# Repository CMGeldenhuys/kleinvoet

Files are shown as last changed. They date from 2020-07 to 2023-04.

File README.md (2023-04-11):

# Kleinvoet





*Kleinvoet* is a self-contained low-cost passive acoustic monitoring device.
The recorder was initially designed for distributed infrasonic (8Hz)
localisation, and features accurate temporal synchronisation through the use of
an onboard GNSS module.

The recorder is capable of 24-bit stereo recording at a variable sampling rate
of 8kHz to 192kHz.  The recordings along with timestamp and operational log
information is stored on a microSD card.  The recordings are stored as a series of
256MiB WAV files.

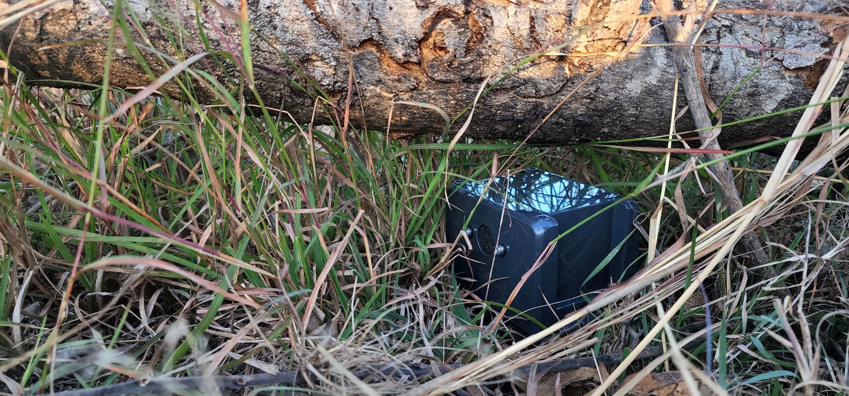
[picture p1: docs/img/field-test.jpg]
Kleinvoet Field Test


Firmware is available at [CMGeldenhuys/kleinvoet-firmware](https://github.com/CMGeldenhuys/kleinvoet-firmware).
All relevant production files such as panelised gerbers, bill of materials and work orders can be found in the `production` folder in the repo.
Additionally, the PCB layout and schematics for the Kleinvoet recorders can be found in the `docs/pcb_single`, `docs/pcb_panel` and `docs/schematics` directories, respectively.

## Example Recordings

- [Artificial elephant call](docs/rec/elephant_call_1000hz_lpf_normalised.wav) (recorded 150m from source, 1000Hz low pass filtered and normalised)

## SD Card Recommendations

In order to keep cost down, Kleinvoet does not make use of external SRAM. As such
the I/O buffer is limited to the internal SRAM of the MCU. It is thus
recommended using a class-10 high quality microSD card. Before a long-running
experiment it is also recommended to do a "low-level" format of the microSD
card. This will improve the write performance which is required at higher
sampling rates.

## Assembly

To assemble a Kleinvoet node, one will require all the electronic
components listed in the bill of materials (BOM), as well as have the necessary
PCBs manufactured. The provided gerber files can be sent directly to most PCB
fabrication houses. To assemble the boards, one can use either hot-air or plate
reflow soldering methods. The [interactive BOM](bom/ibom.html) might be useful
when placing the components manually.

| PCB | Back | Front |
| --- | --- | --- |
|Main Board|  |  |
|GNSS Board|  |  |
|Microphone Board|  |  |

Once all the components have been soldered to their respective boards, the
firmware can be flashed to the MCU using an [ST
Link](https://www.st.com/en/development-tools/st-link-v2.html)
debugger/programmer. However, not tested, any JTAG debugger/programmer should
work. There are also open-source projects that use another STM32 MCU as a
debugger/programmer ([blackmagic
probe](https://github.com/blackmagic-debug/blackmagic)).

Once programmed, proceed by connecting the GNSS header (marked on the respective
PCBs) of the main board to the GNSS daughter board. Note, this connector can be
reversed and the user should double-check that the **SYNC** pin (marked with an
triangle) on the main board is connected to the **SYNC** pin of the GNSS board.
If your use case does not require timestamping, the GNSS board can be omitted.
Next, connect the microphone boards to their respective channels, marked on the
main board's PCB as **CH1** and **CH2**. These connectors are keyed, and thus
It can only be connected one way.

If the user chooses to omit the weatherproof housing, Kleinvoet can be held
together with two rubber bands. The notches on the main and GNSS boards snap
together with the holes in the microphone boards to form a cube.



In order to assemble the weatherproof housing, start by placing the LiPo battery
in the lid of the enclosure. Thread the battery lead through the hole of the
main PCB adaptor plate. Next, mount the plate to the lid, keeping the battery in
place. One can then proceed to mount the main PCB to the adaptor. Next mount
the GNSS adaptor plate in the bottom of the Bocube housing, and mount the GNSS
PCB to the adaptor. If using the windshielding, remove the backing paper and
paste it firmly over the microphone inlets, (Note, the MEMS microphones used are
bottom port microphone and thus the inlet port is on the bottom side of the PCB.
The area to place the shielding foam is marked by a hashed circle) Install the
microphone board spacers, ensuring that the mounting holes align properly. The
microphone board assembly can now be mounted to the inside of the Bocube
housing. Next, connect the individual daughter boards (GNSS and microphone PCBs)
to their respective connectors on the main board.

Insert a FAT32 formatted microSD card into the main board and plug in the
battery. The node will perform a self test, followed by a self configuration
stage and then begin recordings. This process might take up to 10 seconds. Once
the node is configured, a solid amber light will be illuminated. Please refer to
the troubleshooting section if this is not the case.

## Operation

### Startup Procedure

1. Ensure the device is powered off.
1. Insert a FAT32 formatted microSD into the main board.
1. Connect the battery to the main board.
1. Wait for the solid amber indicator LED.
1. (Optional) Close weatherproof housing.

### Shutdown Procedure

1. Press the **USER** button (marked on the PCB of the main board).
1. The status indicators should start flashing repeatedly.
1. Disconnect the battery.
1. Remove microSD card.

### Status Indicators
Each PCB contains a *RED* status LED, used to indicate that the board has power.
On the main PCB there are two running status indication LEDs (*AMBER* and *BLUE*).

When **running**, the *AMBER* LED will remain solid. Once a GNSS lock (both time
and location) is obtained, the *BLUE* LED will pulse briefly every 10 seconds
(default).

If an unrecoverable error has occurred, the two status LEDs (*AMBER* and *BLUE*),
will pulse is quick succession. In this case, the watchdog timer will trigger and
attempt to write the operational log and reset the device. During a catastrophic
failure it might not be possible to write to the microSD card depending on the
error that has occurred.

| State | Blue LED | Amber LED |
| --- | --- | --- |
| Start-up | Blink (1s) | Off |
| Recording | Solid | X |
| GNSS Lock | X | Blink (10s) |
| Catastrophic Error | Strobe | Strobe |

In the table above, '*X*' denotes a "do not care" or irrelevant status. In other
words, it is not an indication of the current device state.

### File Layout

After recording, the following file structure will be present on the microSD card of the respective node.

```
(root)
├── REC_1
│   ├── KV.LOG
│   ├── REC.WAV
│   ├── REC.W01
│   ├── REC.W02
│   ├── REC.W03
│   └── TS.CSV
├── REC_X
│   ├── KV.LOG
│   ├── REC.WXX
│   └── TS.CSV
└── CONF.INI (experimental)
```

Each recording will be stored as a WAVE file in the corresponding `REC_X`
folder. Where the recorder increments `X` for every subsequent recording made on
the device (e.g. `REC_1`, `REC_2` etc.). Inside each recording folder are the
files associated with that recording. Due to the limitation of the FAT32
filesystem each individual recording has to be split up across multiple WAVE
files (e.g.`REC.WAV`, `REC.W01`, etc.). By default, this is in 256 MiB chunks, but
is user configurable Contained in the header of each WAVE file is timestamping
and location information required to synchronise the nodes during offline
processing of the files. A granular log of the timestamping metadata is stored
in `TS.CSV`. A complete operational log is stored in `KV.LOG`, which might deem
useful in troubleshooting a faulty recording node. (Experimental) Currently the
node's configuration is compiled into the device firmware, however, there is a
experimental firmware branch that allows for the configuration to be stored on
the microSD. 

| File/Folder | Purpose |
| --- | --- |
| REC_X | Folder containing all files associated with the particular recording|
| KV.LOG | Operational log of recordings |
| TS.CSV | Timestamping metadata |
| REC.WXX | Audio recording stored as a WAVE file |
| CONF.INI | (Experimental) Runtime configuration file |

## Power Spectral Density Estimates

Provided below are a power spectral density estimates (PSD) generated using
Welch's method. The [Sennheiser MKH 8020](https://sennheiser.com/mkh-8020) was used as a reference microphone and
tested in an acoustically dampened recording studio. These results provide an
estimate of the recording device's frequency response and should not be used
as ground truth measurements where spectral magnitude accuracy is required.
For those types of experiments, we recommenced the use of calibrated reference
sound amplitude measurement equipment.

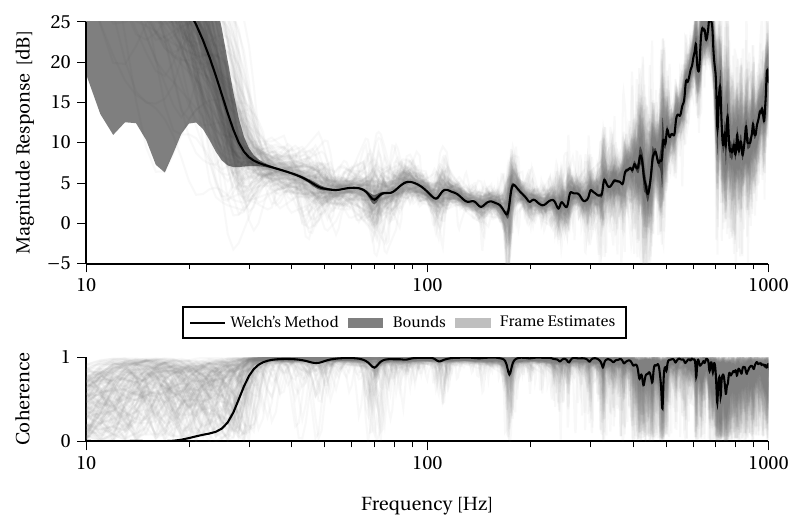
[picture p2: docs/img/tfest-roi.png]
Power Spectral Density Estimate


## Troubleshooting

First ensure the following:
- Power from USB-C not battery, all boards have a solid *RED* LED illuminated
- MicroSD Card is formatted as **FAT32** and inserted
- The respective daughter boards are correctly connected

Enable `LOG_DEST_TTY` in `config.h`. The operational log will be printed in
real-time to the serial console available on the debug/programming port. When
using an *ST Link* debugger, this serial port can be opened using
[Putty](https://www.putty.org/) on Windows, or with the following command on
Linux:
``` sh
screen -b 115200 /dev/ttyACM0
```
The serial port is configured to **115200** baud rate and the standard **8N1**
configuration. Please see the [firmware guide](firmware/README.md) for more
information on setting up the programming environment on a Linux-based system.

## Future Hardware Revisions

- [ ] Dedicated GNSS connector, instead of headers
- [ ] E-Ink Display
- [ ] DFU mode (program without probe)
- [ ] Improved low-power mode (deep sleep)
- [ ] Add BME280 Sensor (temperature, humidity, atmospheric pressure)
- [ ] Battery charging status detection
- [ ] Dedicated power switch
- [ ] External RAM (larger buffer, allows use with low-end SD cards)
- [ ] Allow non-LiPo batteries (eg. alkaline)

## Contributing

We welcome contributions to the project. Unfortunately, hardware cannot be
provided to contributors. However, the [STM32
Nucleo-F446RE](https://www.st.com/en/evaluation-tools/nucleo-f446re.html) can be
used as an firmware development alternative, and is readily available.

## Authors and Acknowledgements

- [Christiaan M. Geldenhuys](https://github.com/CMGeldenhuys)
- [Thomas R. Niesler](https://dsp.sun.ac.za/~trn)

This project formed part of research done by the [Electrical and Electronic
Engineering Department](https://www.ee.sun.ac.za/) at Stellenbosch University.

Stellenbosch University Logo (https://www.ee.sun.ac.za/)

## License

The Kleinvoet project is licensed under the CERN Open Hardware License version 2
(strongly-reciprocal variant). The license agreement and copyright only partain
to the Kleinvoet recorder design. Third party CAD models and EDA footprints
remain under the original license agreement and copyright of the respective
intellectual property owners.

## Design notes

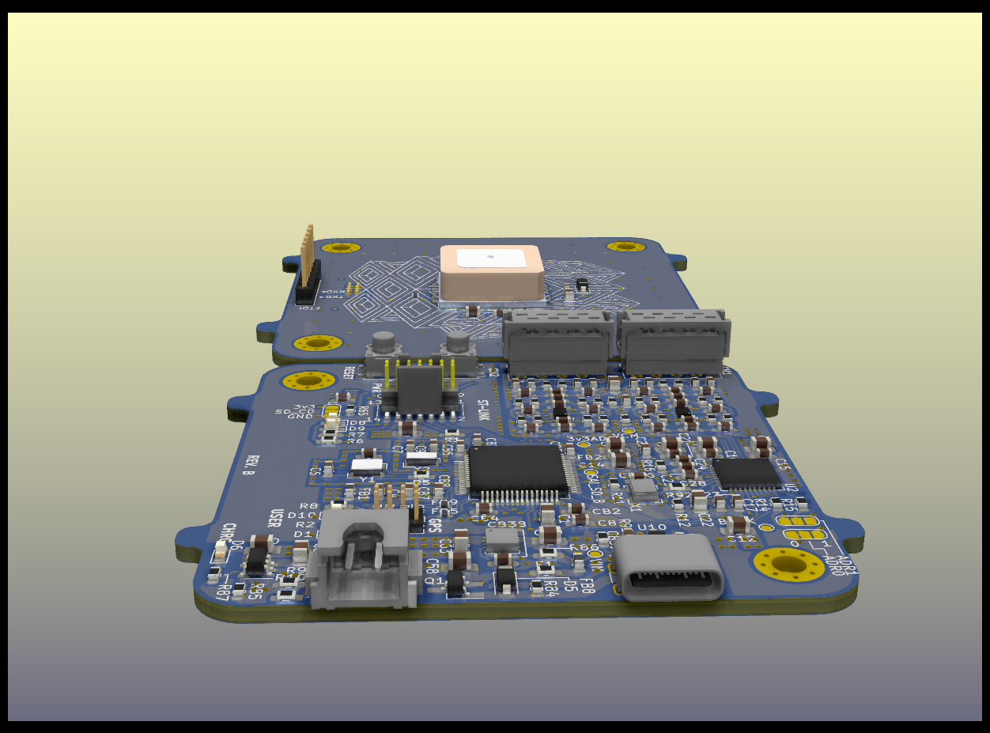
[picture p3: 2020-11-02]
docs/img/kleinvoet_render_3.png

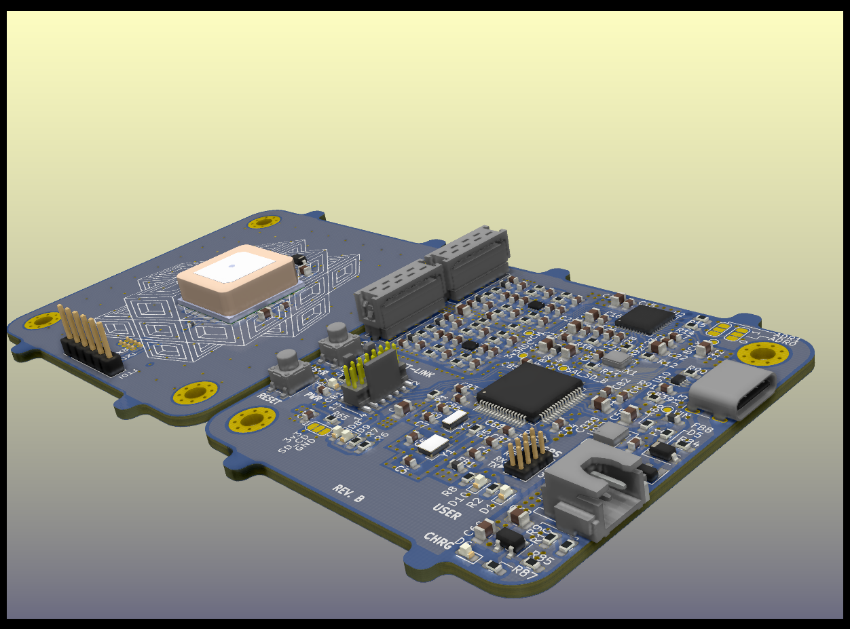
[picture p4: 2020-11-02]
docs/img/kleinvoet_render_0.png

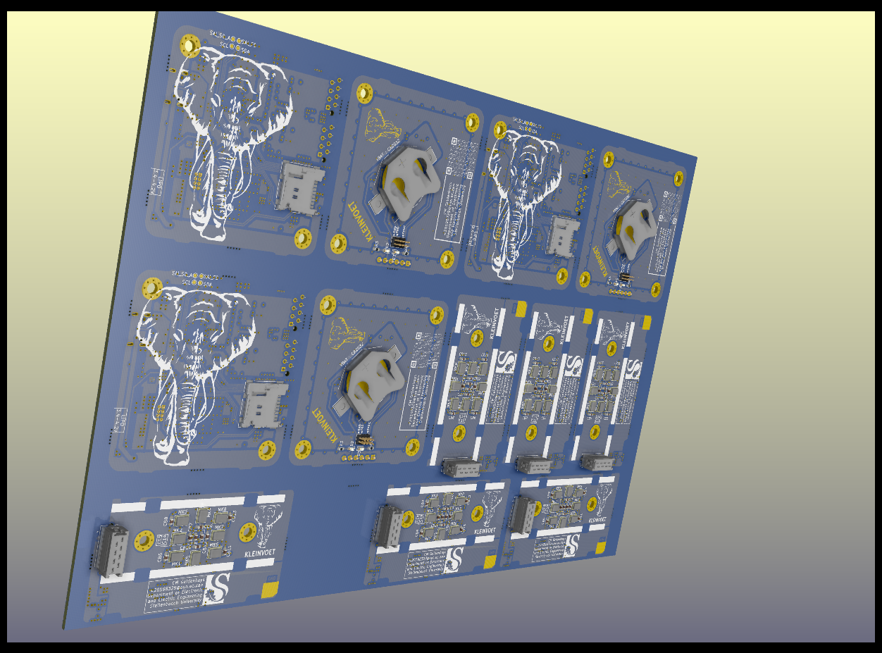
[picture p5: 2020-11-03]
docs/img/panel_render_1.png

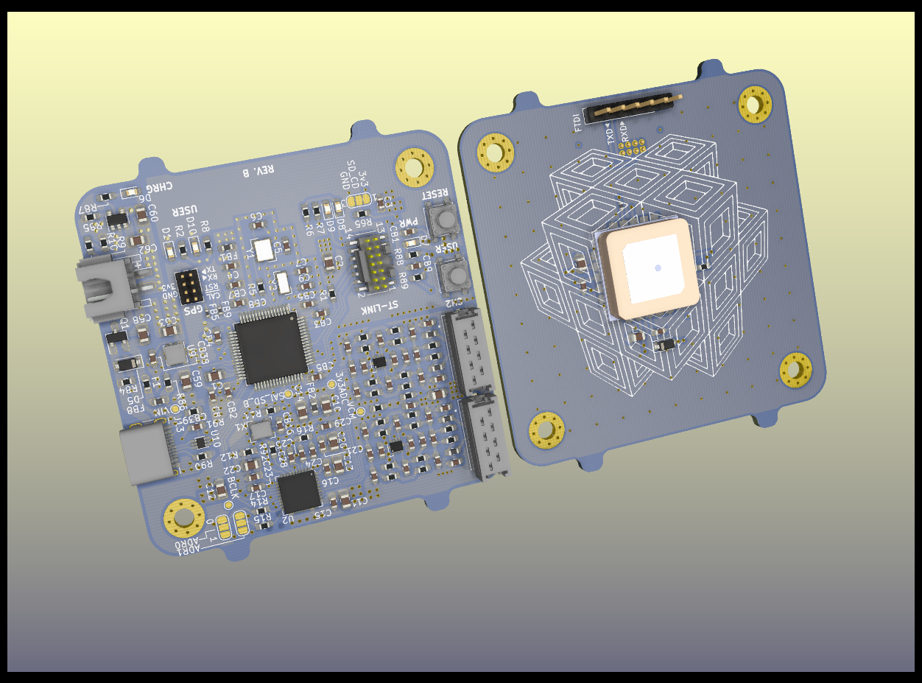
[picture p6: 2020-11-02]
docs/img/kleinvoet_render_1.png

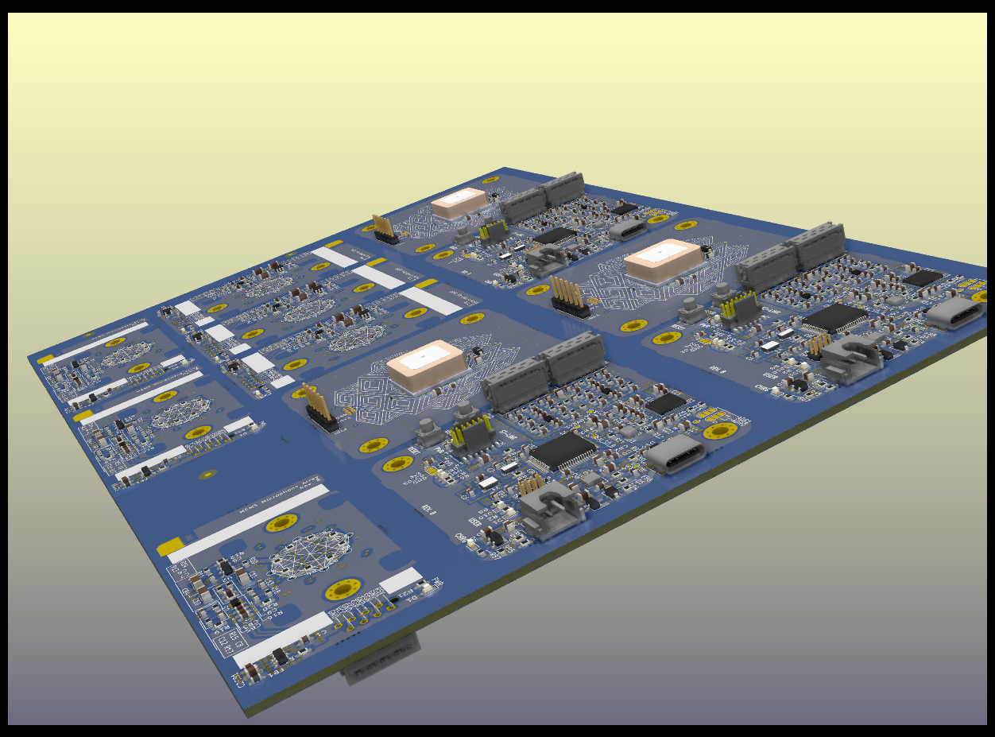
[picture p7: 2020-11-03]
docs/img/panel_render_0.png

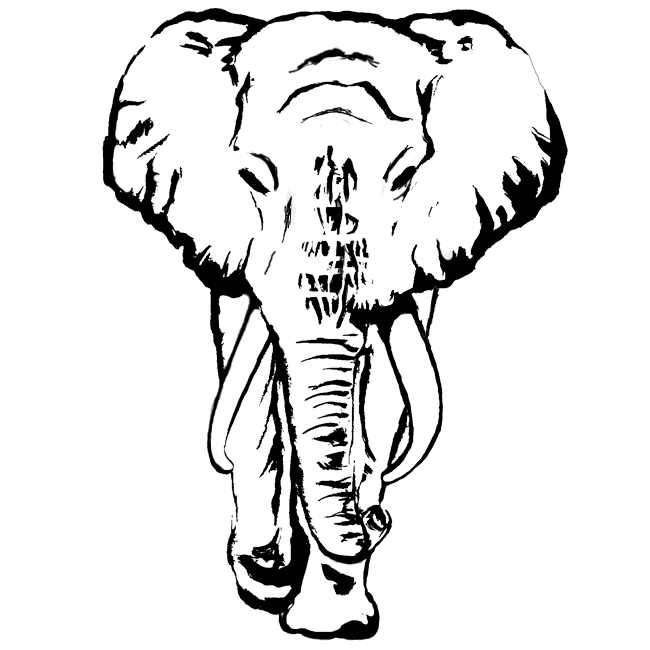
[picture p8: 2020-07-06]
docs/img/oli2.bmp

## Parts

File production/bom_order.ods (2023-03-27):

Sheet: FAB
Received | MPN | Mfr. | Board | Quantity | Value | Reference
1 | 7-215079-8 | TE Connectivity | Sensor_Board_1 | 1 | Sensor_Conn | J1
1 | 7-215083-8 | TE Connectivity | Sensor_Board_1 | 1 | Sensor_Conn | J1
1 | BLM18EG101TZ1D | Murata Electronics | Sensor_Board_1 | 1 | 100 @ 100 MHz | FB1
1 | C0603C104M5RACTU | KEMET | Sensor_Board_1 | 12 | 100n | CB1 CB10 CB11 CB12 CB13 CB3 CB4 CB5 CB6 CB7 CB8 CB9
1 | C0603C105K8RACTU | KEMET | Sensor_Board_1 | 4 | 1u | C1 C14 C15 C3
1 | C0603C221J5GACTU | KEMET | Sensor_Board_1 | 3 | 220p | C12 C13 C5
1 | C0805C106K9PACTU | KEMET | Sensor_Board_1 | 1 | 10u | C2
1 | CC0603JRX7R8BB183 | Yageo | Sensor_Board_1 | 1 | 18n | C6
1 | CC0603JRX7R9BB272 | Yageo | Sensor_Board_1 | 2 | 2.7n | C8 C9
1 | ERJ-3EKF1001V | Panasonic | Sensor_Board_1 | 2 | 1k0 | R17 R18
1 | ERJ-3EKF2100V | Panasonic | Sensor_Board_1 | 1 | 210 | R14
1 | ERJ-3EKF2201V | Panasonic | Sensor_Board_1 | 11 | 2k2 | R11 R12 R2 R21 R3 R4 R5 R6 R7 R8 R9
1 | ERJ-3EKF2700V | Panasonic | Sensor_Board_1 | 1 | 270 | R13
1 | ERJ-3EKF3300V | Panasonic | Sensor_Board_1 | 2 | 330 | R15 R16
1 | ERJ-3EKF47R0V | Panasonic | Sensor_Board_1 | 2 | 47 | R19 R20
1 | GRM31CR60J107KE39K | Murata Electronics | Sensor_Board_1 | 3 | 47u | C10 C11 C4
1 | ICS-40300 | TDK InvenSense | Sensor_Board_1 | 9 | TestPoint | MK1 MK2 MK3 MK4 MK5 MK6 MK7 MK8 TP1
1 | OPA377AIDBVR | Texas Instruments | Sensor_Board_1 | 1 | OPA377xxDBVx | U2
1 | RC0603JR-0710KL | Yageo | Sensor_Board_1 | 1 | 10k | R1
1 | SML-D12U8WT86C | ROHM Semiconductor | Sensor_Board_1 | 1 | RED | D1
1 | THS4551IRUNR | Texas Instruments | Sensor_Board_1 | 1 | THS4551 | U3
1 | TLV74118PDBVR | Texas Instruments | Sensor_Board_1 | 1 | TLV741PxxDBVx | U1
1 | 7-215079-8 | TE Connectivity | Sensor_Board_2 | 1 | Sensor_Conn | J1
1 | 7-215083-8 | TE Connectivity | Sensor_Board_2 | 1 | Sensor_Conn | J1
1 | BLM18EG101TZ1D | Murata Electronics | Sensor_Board_2 | 1 | 100 @ 100 MHz | FB1
1 | C0603C104M5RACTU | KEMET | Sensor_Board_2 | 12 | 100n | CB1 CB10 CB11 CB12 CB13 CB3 CB4 CB5 CB6 CB7 CB8 CB9
1 | C0603C105K8RACTU | KEMET | Sensor_Board_2 | 4 | 1u | C1 C14 C15 C3
1 | C0603C221J5GACTU | KEMET | Sensor_Board_2 | 3 | 220p | C12 C13 C5
1 | C0805C106K9PACTU | KEMET | Sensor_Board_2 | 1 | 10u | C2
1 | CC0603JRX7R8BB183 | Yageo | Sensor_Board_2 | 1 | 18n | C6
1 | CC0603JRX7R9BB272 | Yageo | Sensor_Board_2 | 2 | 2.7n | C8 C9
1 | ERJ-3EKF1001V | Panasonic | Sensor_Board_2 | 2 | 1k0 | R17 R18
1 | ERJ-3EKF2100V | Panasonic | Sensor_Board_2 | 1 | 210 | R14
1 | ERJ-3EKF2201V | Panasonic | Sensor_Board_2 | 11 | 2k2 | R11 R12 R2 R21 R3 R4 R5 R6 R7 R8 R9
1 | ERJ-3EKF2700V | Panasonic | Sensor_Board_2 | 1 | 270 | R13
1 | ERJ-3EKF3300V | Panasonic | Sensor_Board_2 | 2 | 330 | R15 R16
1 | ERJ-3EKF47R0V | Panasonic | Sensor_Board_2 | 2 | 47 | R19 R20
1 | GRM31CR60J107KE39K | Murata Electronics | Sensor_Board_2 | 3 | 47u | C10 C11 C4
1 | ICS-40300 | TDK InvenSense | Sensor_Board_2 | 9 | TestPoint | MK1 MK2 MK3 MK4 MK5 MK6 MK7 MK8 TP1
1 | OPA377AIDBVR | Texas Instruments | Sensor_Board_2 | 1 | OPA377xxDBVx | U2
1 | RC0603JR-0710KL | Yageo | Sensor_Board_2 | 1 | 10k | R1
1 | SML-D12U8WT86C | ROHM Semiconductor | Sensor_Board_2 | 1 | RED | D1
1 | THS4551IRUNR | Texas Instruments | Sensor_Board_2 | 1 | THS4551 | U3
1 | TLV74118PDBVR | Texas Instruments | Sensor_Board_2 | 1 | TLV741PxxDBVx | U1
1 | 0ZCM0020FF2G | Bel Fuse | kleinvoet | 1 | 400mA | F1
1 | 1769 | Adafruit | kleinvoet | 1 | JST-PH | J12
1 | 2898 | Keystone Electronics | kleinvoet | 1 | COIN_BAT | BT1
1 | 7-215079-8 | TE Connectivity | kleinvoet | 2 | Sensor_Conn | J3 J6
1 | 7-215083-8 | TE Connectivity | kleinvoet | 2 | Sensor_Conn | J3 J6
1 | AC0603FR-135K1L | Yageo | kleinvoet | 3 | 5.1k | R85 R90 R91
1 | ADAU1978WBCPZ-RL | Analog Devices | kleinvoet | 1 | ADAU1978 | U2
1 | BLM15HD102SN1D | Murata Electronics | kleinvoet | 3 | BLM15HD102SN1 | FB10 FB5 FB9
1 | BLM18EG101TZ1D | Murata Electronics | kleinvoet | 1 | 100 @ 100 MHz | FB8
1 | BLM18KG101TZ1D | Murata Electronics | kleinvoet | 2 | BLM18KG101TZ1D | FB1 FB2
1 | BLM18KG102SN1D | Murata Electronics | kleinvoet | 4 | 1k @ 100 MHz | FB11 FB3 FB4 FB7
1 | C0603C103J5RACTU | KEMET | kleinvoet | 6 | 10n | C42 C44 C76 C78 CB38 CB8
1 | C0603C104M5RACTU | KEMET | kleinvoet | 24 | 100n | C15 C16 C17 C21 C23 C28 C29 C37 C40 C43 C71 C74 C77 CB1 CB16 CB2 CB3 CB39 CB4 CB40 CB5 CB6 CB7 CB9
1 | C0603C105K8RACTU | KEMET | kleinvoet | 5 | 1u | C3 C32 C4 C66 C8
1 | C0603C150J5GACTU | KEMET | kleinvoet | 2 | 15pF | C5 C6
1 | C0603C221J5GACTU | KEMET | kleinvoet | 8 | 220p | C18 C19 C26 C27 C30 C31 C61 C67
1 | C0805C106K9PACTU | KEMET | kleinvoet | 17 | 10u | C1 C10 C11 C12 C13 C14 C2 C20 C22 C33 C58 C59 C60 C62 C63 C64 C65
1 | C1608C0G1H040C080AA | TDK | kleinvoet | 2 | 4p | C7 C9
1 | CC0603JRNPO9BN391 | Yageo | kleinvoet | 1 | 390p | C25
1 | CC0603JRX7R9BB273 | Yageo | kleinvoet | 2 | 27n | C34 C68
1 | CC0603JRX7R9BB392 | Yageo | kleinvoet | 4 | 3.9n | C38 C39 C72 C73
1 | CC0603JRX7R9BB562 | Yageo | kleinvoet | 1 | 5.6n | C24
1 | DX07S016JA1R1500 | JAE Electronics | kleinvoet | 1 | USB_C_Receptacle_USB2.0 | J13
1 | ECS-.327-7-34B-TR | ECS | kleinvoet | 1 | 32.768 kHz | Y2
1 | ECS-120-12-33-AEN-TR | ECS | kleinvoet | 1 | 12 MHz | Y1
1 | ECS-TXO-3225MV-122.8-TR | ECS | kleinvoet | 1 | 12.288MHz | X1
1 | ERJ-3EKF15R0V | Panasonic | kleinvoet | 4 | 15 | R25 R26 R49 R50
1 | ERJ-3EKF3090V | Panasonic | kleinvoet | 4 | 310 | R17 R18 R41 R42
1 | ERJ-3EKF3300V | Panasonic | kleinvoet | 4 | 330 | R21 R22 R45 R46
1 | ERJ-3EKF3600V | Panasonic | kleinvoet | 4 | 360 | R23 R24 R47 R48
1 | ERJ-3EKF47R0V | Panasonic | kleinvoet | 6 | 47 | R20 R27 R28 R51 R52 R92
1 | FTSH-104-01-F-D | Samtec | kleinvoet | 2 | GPS_Transmission_Conn | J16 J4
1 | FTSH-107-01-F-DV-K | Samtec | kleinvoet | 1 | Conn_ST_STDC14 | J1
1 | MCP73831T-2ACI/OT | Microchip | kleinvoet | 1 | MCP73831-2-OT | U8
1 | NTR3A30PZT1G | ON Semiconductor | kleinvoet | 1 | PMOS | Q1
1 | PTS647SN50SMTR2LFS | C&K | kleinvoet | 2 | USER | SW1 SW2
1 | RC0603FR-07100KL | Yageo | kleinvoet | 4 | 100k | R13 R19 R65 R84
1 | RC0603FR-071KL | Yageo | kleinvoet | 1 | 1k | R16
1 | RC0603FR-072K2L | Yageo | kleinvoet | 8 | 2.2k | R2 R3 R4 R6 R7 R8 R87 R88
1 | RC0603FR-07470KL | Yageo | kleinvoet | 2 | 500k | R10 R9
1 | RC0603FR-1068RL | Yageo | kleinvoet | 1 | 68 | R5
1 | RC0603JR-0710KL | Yageo | kleinvoet | 7 | 10k | R1 R11 R12 R14 R15 R86 R89
1 | RSX101MM-30TR | ROHM Semiconductor | kleinvoet | 2 | Vf low | D4 D5
1 | SML-D12D8WT86C | ROHM Semiconductor | kleinvoet | 2 | ORANGE | D10 D6
1 | SML-D12U8WT86C | ROHM Semiconductor | kleinvoet | 1 | RED | D7
1 | SML-D12Y8WT86C | ROHM Semiconductor | kleinvoet | 2 | YELLOW | D3 D9
1 | SMLD12BN1WT86 | ROHM Semiconductor | kleinvoet | 1 | BLUE | D1
1 | SMLD12EN1WT86 | ROHM Semiconductor | kleinvoet | 2 | GREEN | D2 D8
1 | STM32F446RCT6 | STMicroelectronics | kleinvoet | 1 | STM32F446RETx | U1
1 | THS4551IRUNR | Texas Instruments | kleinvoet | 2 | THS4551 | U3 U5
1 | TPS73733QDRBRQ1 | Texas Instruments | kleinvoet | 1 | TPS73733QDRBRQ1 | U9
1 | USBLC6-2P6 | STMicroelectronics | kleinvoet | 1 | USBLC6-2SC6 | U10

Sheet: Data
Board | Reference | Value | Footprint | Datasheet | MPN | Mfr. | Notes
kleinvoet | C2 | 10u | Capacitor_SMD:C_0805_2012Metric_Pad1.18x1.45mm_HandSolder | ~ | C0805C106K9PACTU | KEMET | Low ESR
kleinvoet | CB2 | 100n | Capacitor_SMD:C_0603_1608Metric_Pad1.08x0.95mm_HandSolder | ~ | C0603C104M5RACTU | KEMET
kleinvoet | FB1 | BLM18KG101TZ1D | Inductor_SMD:L_0603_1608Metric_Pad1.05x0.95mm_HandSolder | ~ | BLM18KG101TZ1D | Murata Electronics | 100 @ 100 MHz
kleinvoet | CB7 | 100n | Capacitor_SMD:C_0603_1608Metric_Pad1.08x0.95mm_HandSolder | ~ | C0603C104M5RACTU | KEMET | Low ESR (X7R)
kleinvoet | C4 | 1u | Capacitor_SMD:C_0603_1608Metric_Pad1.08x0.95mm_HandSolder | ~ | C0603C105K8RACTU | KEMET | Low ESR (X7R)
kleinvoet | CB8 | 10n | Capacitor_SMD:C_0603_1608Metric_Pad1.08x0.95mm_HandSolder | ~ | C0603C103J5RACTU | KEMET | Low ESR (X7R)
kleinvoet | CB3 | 100n | Capacitor_SMD:C_0603_1608Metric_Pad1.08x0.95mm_HandSolder | ~ | C0603C104M5RACTU | KEMET
kleinvoet | CB4 | 100n | Capacitor_SMD:C_0603_1608Metric_Pad1.08x0.95mm_HandSolder | ~ | C0603C104M5RACTU | KEMET
kleinvoet | CB5 | 100n | Capacitor_SMD:C_0603_1608Metric_Pad1.08x0.95mm_HandSolder | ~ | C0603C104M5RACTU | KEMET
kleinvoet | CB1 | 100n | Capacitor_SMD:C_0603_1608Metric_Pad1.08x0.95mm_HandSolder | ~ | C0603C104M5RACTU | KEMET
kleinvoet | J1 | Conn_ST_STDC14 | grootvoet:SAMTEC-FTSH-107-01-X-DV | https://www.st.com/content/ccc/resource/technical/document/user_manual/group1/99/49/91/b6/b2/3a/46/e5/DM00526767/files/DM00526767.pdf/jcr:content/translations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 | FTSH-107-01-F-DV-K | Samtec
kleinvoet | R2 | 2.2k | Resistor_SMD:R_0603_1608Metric_Pad0.98x0.95mm_HandSolder | ~ | RC0603FR-072K2L | Yageo
kleinvoet | D1 | BLUE | LED_SMD:LED_0603_1608Metric_Pad1.05x0.95mm_HandSolder | ~ | SMLD12BN1WT86 | ROHM Semiconductor
kleinvoet | C1 | 10u | Capacitor_SMD:C_0805_2012Metric_Pad1.18x1.45mm_HandSolder | ~ | C0805C106K9PACTU | KEMET | Low ESR (< 1 Ohm)
kleinvoet | R1 | 10k | Resistor_SMD:R_0603_1608Metric_Pad0.98x0.95mm_HandSolder | ~ | RC0603JR-0710KL | Yageo
kleinvoet | Y1 | 12 MHz | grootvoet:ECS-33B | https://www.mouser.co.za/datasheet/2/122/ECS-33B-1649459.pdf | ECS-120-12-33-AEN-TR | ECS
kleinvoet | C5 | 15pF | Capacitor_SMD:C_0603_1608Metric_Pad1.08x0.95mm_HandSolder | ~ | C0603C150J5GACTU | KEMET | C0G - High freq.
kleinvoet | C6 | 15pF | Capacitor_SMD:C_0603_1608Metric_Pad1.08x0.95mm_HandSolder | ~ | C0603C150J5GACTU | KEMET | C0G - High freq.
kleinvoet | R5 | 68 | Resistor_SMD:R_0603_1608Metric_Pad0.98x0.95mm_HandSolder | ~ | RC0603FR-1068RL | Yageo
kleinvoet | Y2 | 32.768 kHz | grootvoet:ECX-31B | ~ | ECS-.327-7-34B-TR | ECS
kleinvoet | C7 | 4p | Capacitor_SMD:C_0603_1608Metric_Pad1.08x0.95mm_HandSolder | ~ | C1608C0G1H040C080AA | TDK | C0G
kleinvoet | C9 | 4p | Capacitor_SMD:C_0603_1608Metric_Pad1.08x0.95mm_HandSolder | ~ | C1608C0G1H040C080AA | TDK | C0G
kleinvoet | R9 | 500k | Resistor_SMD:R_0603_1608Metric_Pad0.98x0.95mm_HandSolder | ~ | RC0603FR-07470KL | Yageo
kleinvoet | R10 | 500k | Resistor_SMD:R_0603_1608Metric_Pad0.98x0.95mm_HandSolder | ~ | RC0603FR-07470KL | Yageo
kleinvoet | C8 | 1u | Capacitor_SMD:C_0603_1608Metric_Pad1.08x0.95mm_HandSolder | ~ | C0603C105K8RACTU | KEMET
kleinvoet | SW2 | USER | grootvoet:SW_SPST_PTS647 | ~ | PTS647SN50SMTR2LFS | C&K
kleinvoet | CB9 | 100n | Capacitor_SMD:C_0603_1608Metric_Pad1.08x0.95mm_HandSolder | ~ | C0603C104M5RACTU | KEMET
kleinvoet | SW1 | RESET | grootvoet:SW_SPST_PTS647 | ~ | PTS647SN50SMTR2LFS | C&K
kleinvoet | FB9 | BLM15HD102SN1 | Inductor_SMD:L_0603_1608Metric_Pad1.05x0.95mm_HandSolder | ~ | BLM15HD102SN1D | Murata Electronics
kleinvoet | CB6 | 100n | Capacitor_SMD:C_0603_1608Metric_Pad1.08x0.95mm_HandSolder | ~ | C0603C104M5RACTU | KEMET
kleinvoet | U1 | STM32F446RETx | Package_QFP:LQFP-64_10x10mm_P0.5mm | http://www.st.com/st-web-ui/static/active/en/resource/technical/document/datasheet/DM00141306.pdf | STM32F446RCT6 | STMicroelectronics
kleinvoet | R6 | 2.2k | Resistor_SMD:R_0603_1608Metric_Pad0.98x0.95mm_HandSolder | ~ | RC0603FR-072K2L | Yageo
kleinvoet | D8 | GREEN | LED_SMD:LED_0603_1608Metric_Pad1.05x0.95mm_HandSolder | ~ | SMLD12EN1WT86 | ROHM Semiconductor
kleinvoet | R7 | 2.2k | Resistor_SMD:R_0603_1608Metric_Pad0.98x0.95mm_HandSolder | ~ | RC0603FR-072K2L | Yageo
kleinvoet | D9 | YELLOW | LED_SMD:LED_0603_1608Metric_Pad1.05x0.95mm_HandSolder | ~ | SML-D12Y8WT86C | ROHM Semiconductor
kleinvoet | D10 | ORANGE | LED_SMD:LED_0603_1608Metric_Pad1.05x0.95mm_HandSolder | ~ | SML-D12D8WT86C | ROHM Semiconductor
kleinvoet | R8 | 2.2k | Resistor_SMD:R_0603_1608Metric_Pad0.98x0.95mm_HandSolder | ~ | RC0603FR-072K2L | Yageo
kleinvoet | FB5 | BLM15HD102SN1 | Inductor_SMD:L_0603_1608Metric_Pad1.05x0.95mm_HandSolder | ~ | BLM15HD102SN1D | Murata Electronics
kleinvoet | FB2 | BLM18KG101TZ1D | Inductor_SMD:L_0603_1608Metric_Pad1.05x0.95mm_HandSolder | ~ | BLM18KG101TZ1D | Murata Electronics | 1k @ 100 MHz
kleinvoet | CB16 | 100n | Capacitor_SMD:C_0603_1608Metric_Pad1.08x0.95mm_HandSolder | ~ | C0603C104M5RACTU | KEMET
kleinvoet | C11 | 10u | Capacitor_SMD:C_0805_2012Metric_Pad1.18x1.45mm_HandSolder | ~ | C0805C106K9PACTU | KEMET | Low ESR (X7R)
kleinvoet | C12 | 10u | Capacitor_SMD:C_0805_2012Metric_Pad1.18x1.45mm_HandSolder | ~ | C0805C106K9PACTU | KEMET | Low ESR (X7R)
kleinvoet | R92 | 47 | Resistor_SMD:R_0603_1608Metric_Pad0.98x0.95mm_HandSolder | ~ | ERJ-3EKF47R0V | Panasonic
kleinvoet | C10 | 10u | Capacitor_SMD:C_0805_2012Metric_Pad1.18x1.45mm_HandSolder | ~ | C0805C106K9PACTU | KEMET | Low ESR (X7R)
kleinvoet | C13 | 10u | Capacitor_SMD:C_0805_2012Metric_Pad1.18x1.45mm_HandSolder | ~ | C0805C106K9PACTU | KEMET | Low ESR (X7R)
kleinvoet | X1 | 12.288MHz | grootvoet:ECS-TXO-3225MV |  | ECS-TXO-3225MV-122.8-TR | ECS
kleinvoet | C20 | 10u | Capacitor_SMD:C_0805_2012Metric_Pad1.18x1.45mm_HandSolder | ~ | C0805C106K9PACTU | KEMET | Low ESR (X7R)
kleinvoet | C21 | 100n | Capacitor_SMD:C_0603_1608Metric_Pad1.08x0.95mm_HandSolder | ~ | C0603C104M5RACTU | KEMET
kleinvoet | C15 | 100n | Capacitor_SMD:C_0603_1608Metric_Pad1.08x0.95mm_HandSolder | ~ | C0603C104M5RACTU | KEMET
kleinvoet | C16 | 100n | Capacitor_SMD:C_0603_1608Metric_Pad1.08x0.95mm_HandSolder | ~ | C0603C104M5RACTU | KEMET
kleinvoet | C17 | 100n | Capacitor_SMD:C_0603_1608Metric_Pad1.08x0.95mm_HandSolder | ~ | C0603C104M5RACTU | KEMET
kleinvoet | C22 | 10u | Capacitor_SMD:C_0805_2012Metric_Pad1.18x1.45mm_HandSolder | ~ | C0805C106K9PACTU | KEMET | Low ESR (X7R)
kleinvoet | C23 | 100n | Capacitor_SMD:C_0603_1608Metric_Pad1.08x0.95mm_HandSolder | ~ | C0603C104M5RACTU | KEMET
kleinvoet | R12 | 10k | Resistor_SMD:R_0603_1608Metric_Pad0.98x0.95mm_HandSolder | ~ | RC0603JR-0710KL | Yageo
kleinvoet | C14 | 10u | Capacitor_SMD:C_0805_2012Metric_Pad1.18x1.45mm_HandSolder | ~ | C0805C106K9PACTU | KEMET | Low ESR (X7R)
kleinvoet | C24 | 5.6n | Capacitor_SMD:C_0603_1608Metric_Pad1.08x0.95mm_HandSolder | ~ | CC0603JRX7R9BB562 | Yageo | NP0
kleinvoet | C25 | 390p | Capacitor_SMD:C_0603_1608Metric_Pad1.08x0.95mm_HandSolder | ~ | CC0603JRNPO9BN391 | Yageo
kleinvoet | R16 | 1k | Resistor_SMD:R_0603_1608Metric_Pad0.98x0.95mm_HandSolder | ~ | RC0603FR-071KL | Yageo
kleinvoet | U2 | ADAU1978 | grootvoet:LFCSP-WQ-40-1EP_6x6mm_P0.5_CP-40-14 |  | ADAU1978WBCPZ-RL | Analog Devices
kleinvoet | R14 | 10k | Resistor_SMD:R_0603_1608Metric_Pad0.98x0.95mm_HandSolder | ~ | RC0603JR-0710KL | Yageo
kleinvoet | R15 | 10k | Resistor_SMD:R_0603_1608Metric_Pad0.98x0.95mm_HandSolder | ~ | RC0603JR-0710KL | Yageo
kleinvoet | JP7 | ADDR0 | Jumper:SolderJumper-3_P1.3mm_Bridged12_RoundedPad1.0x1.5mm_NumberLabels | ~
kleinvoet | JP6 | ADDR1 | Jumper:SolderJumper-3_P1.3mm_Bridged12_RoundedPad1.0x1.5mm_NumberLabels | ~
kleinvoet | R11 | 10k | Resistor_SMD:R_0603_1608Metric_Pad0.98x0.95mm_HandSolder | ~ | RC0603JR-0710KL | Yageo
kleinvoet | TP1 | VADC | TestPoint:TestPoint_Pad_D1.0mm | ~
kleinvoet | TP6 | BCLK | TestPoint:TestPoint_Pad_D1.0mm | ~
kleinvoet | TP7 | FCLK | TestPoint:TestPoint_Pad_D1.0mm | ~
kleinvoet | TP8 | SD1 | TestPoint:TestPoint_Pad_D1.0mm | ~
kleinvoet | TP9 | SD2 | TestPoint:TestPoint_Pad_D1.0mm | ~
kleinvoet | TP10 | SDA | TestPoint:TestPoint_Pad_D1.0mm | ~
kleinvoet | TP11 | SCL | TestPoint:TestPoint_Pad_D1.0mm | ~
kleinvoet | C28 | 100n | Capacitor_SMD:C_0603_1608Metric_Pad1.08x0.95mm_HandSolder | ~ | C0603C104M5RACTU | KEMET
kleinvoet | C29 | 100n | Capacitor_SMD:C_0603_1608Metric_Pad1.08x0.95mm_HandSolder | ~ | C0603C104M5RACTU | KEMET
kleinvoet | R13 | 100k | Resistor_SMD:R_0603_1608Metric_Pad0.98x0.95mm_HandSolder | ~ | RC0603FR-07100KL | Yageo
kleinvoet | R19 | 100k | Resistor_SMD:R_0603_1608Metric_Pad0.98x0.95mm_HandSolder | ~ | RC0603FR-07100KL | Yageo
kleinvoet | C32 | 1u | Capacitor_SMD:C_0603_1608Metric_Pad1.08x0.95mm_HandSolder | ~ | C0603C105K8RACTU | KEMET
kleinvoet | TP2 | VCM | TestPoint:TestPoint_Pad_D1.0mm | ~
kleinvoet | C33 | 10u | Capacitor_SMD:C_0805_2012Metric_Pad1.18x1.45mm_HandSolder | ~ | C0805C106K9PACTU | KEMET | Low ESR (X7R)
kleinvoet | R17 | 310 | Resistor_SMD:R_0603_1608Metric_Pad0.98x0.95mm_HandSolder | ~ | ERJ-3EKF3090V | Panasonic
kleinvoet | R21 | 330 | Resistor_SMD:R_0603_1608Metric_Pad0.98x0.95mm_HandSolder | ~ | ERJ-3EKF3300V | Panasonic
kleinvoet | R23 | 360 | Resistor_SMD:R_0603_1608Metric_Pad0.98x0.95mm_HandSolder | ~ | ERJ-3EKF3600V | Panasonic
kleinvoet | R25 | 15 | Resistor_SMD:R_0603_1608Metric_Pad0.98x0.95mm_HandSolder | ~ | ERJ-3EKF15R0V | Panasonic
kleinvoet | C38 | 3.9n | Capacitor_SMD:C_0603_1608Metric_Pad1.08x0.95mm_HandSolder | ~ | CC0603JRX7R9BB392 | Yageo
kleinvoet | C26 | 220p | Capacitor_SMD:C_0603_1608Metric_Pad1.08x0.95mm_HandSolder | ~ | C0603C221J5GACTU | KEMET
kleinvoet | R18 | 310 | Resistor_SMD:R_0603_1608Metric_Pad0.98x0.95mm_HandSolder | ~ | ERJ-3EKF3090V | Panasonic
kleinvoet | R22 | 330 | Resistor_SMD:R_0603_1608Metric_Pad0.98x0.95mm_HandSolder | ~ | ERJ-3EKF3300V | Panasonic
kleinvoet | R24 | 360 | Resistor_SMD:R_0603_1608Metric_Pad0.98x0.95mm_HandSolder | ~ | ERJ-3EKF3600V | Panasonic
kleinvoet | U3 | THS4551 | grootvoet:WQFN-10_RUN |  | THS4551IRUNR | Texas Instruments
kleinvoet | R26 | 15 | Resistor_SMD:R_0603_1608Metric_Pad0.98x0.95mm_HandSolder | ~ | ERJ-3EKF15R0V | Panasonic
kleinvoet | C39 | 3.9n | Capacitor_SMD:C_0603_1608Metric_Pad1.08x0.95mm_HandSolder | ~ | CC0603JRX7R9BB392 | Yageo
kleinvoet | C35 | OPEN | Capacitor_SMD:C_0603_1608Metric_Pad1.08x0.95mm_HandSolder | ~
kleinvoet | C34 | 27n | Capacitor_SMD:C_0603_1608Metric_Pad1.08x0.95mm_HandSolder | ~ | CC0603JRX7R9BB273 | Yageo
kleinvoet | C27 | 220p | Capacitor_SMD:C_0603_1608Metric_Pad1.08x0.95mm_HandSolder | ~ | C0603C221J5GACTU | KEMET
kleinvoet | C43 | 100n | Capacitor_SMD:C_0603_1608Metric_Pad1.08x0.95mm_HandSolder | ~ | C0603C104M5RACTU | KEMET
kleinvoet | R27 | 47 | Resistor_SMD:R_0603_1608Metric_Pad0.98x0.95mm_HandSolder | ~ | ERJ-3EKF47R0V | Panasonic
kleinvoet | R28 | 47 | Resistor_SMD:R_0603_1608Metric_Pad0.98x0.95mm_HandSolder | ~ | ERJ-3EKF47R0V | Panasonic
kleinvoet | C42 | 10n | Capacitor_SMD:C_0603_1608Metric_Pad1.08x0.95mm_HandSolder | ~ | C0603C103J5RACTU | KEMET
kleinvoet | C44 | 10n | Capacitor_SMD:C_0603_1608Metric_Pad1.08x0.95mm_HandSolder | ~ | C0603C103J5RACTU | KEMET
kleinvoet | C37 | 100n | Capacitor_SMD:C_0603_1608Metric_Pad1.08x0.95mm_HandSolder | ~ | C0603C104M5RACTU | KEMET
kleinvoet | C40 | 100n | Capacitor_SMD:C_0603_1608Metric_Pad1.08x0.95mm_HandSolder | ~ | C0603C104M5RACTU | KEMET
kleinvoet | R41 | 310 | Resistor_SMD:R_0603_1608Metric_Pad0.98x0.95mm_HandSolder | ~ | ERJ-3EKF3090V | Panasonic
kleinvoet | R45 | 330 | Resistor_SMD:R_0603_1608Metric_Pad0.98x0.95mm_HandSolder | ~ | ERJ-3EKF3300V | Panasonic
kleinvoet | R47 | 360 | Resistor_SMD:R_0603_1608Metric_Pad0.98x0.95mm_HandSolder | ~ | ERJ-3EKF3600V | Panasonic
kleinvoet | R49 | 15 | Resistor_SMD:R_0603_1608Metric_Pad0.98x0.95mm_HandSolder | ~ | ERJ-3EKF15R0V | Panasonic
kleinvoet | C72 | 3.9n | Capacitor_SMD:C_0603_1608Metric_Pad1.08x0.95mm_HandSolder | ~ | CC0603JRX7R9BB392 | Yageo
kleinvoet | C61 | 220p | Capacitor_SMD:C_0603_1608Metric_Pad1.08x0.95mm_HandSolder | ~ | C0603C221J5GACTU | KEMET
kleinvoet | R42 | 310 | Resistor_SMD:R_0603_1608Metric_Pad0.98x0.95mm_HandSolder | ~ | ERJ-3EKF3090V | Panasonic
kleinvoet | R46 | 330 | Resistor_SMD:R_0603_1608Metric_Pad0.98x0.95mm_HandSolder | ~ | ERJ-3EKF3300V | Panasonic
kleinvoet | R48 | 360 | Resistor_SMD:R_0603_1608Metric_Pad0.98x0.95mm_HandSolder | ~ | ERJ-3EKF3600V | Panasonic
kleinvoet | U5 | THS4551 | grootvoet:WQFN-10_RUN |  | THS4551IRUNR | Texas Instruments
kleinvoet | R50 | 15 | Resistor_SMD:R_0603_1608Metric_Pad0.98x0.95mm_HandSolder | ~ | ERJ-3EKF15R0V | Panasonic
kleinvoet | C73 | 3.9n | Capacitor_SMD:C_0603_1608Metric_Pad1.08x0.95mm_HandSolder | ~ | CC0603JRX7R9BB392 | Yageo
kleinvoet | C69 | OPEN | Capacitor_SMD:C_0603_1608Metric_Pad1.08x0.95mm_HandSolder | ~
kleinvoet | C68 | 27n | Capacitor_SMD:C_0603_1608Metric_Pad1.08x0.95mm_HandSolder | ~ | CC0603JRX7R9BB273 | Yageo
kleinvoet | C67 | 220p | Capacitor_SMD:C_0603_1608Metric_Pad1.08x0.95mm_HandSolder | ~ | C0603C221J5GACTU | KEMET
kleinvoet | C77 | 100n | Capacitor_SMD:C_0603_1608Metric_Pad1.08x0.95mm_HandSolder | ~ | C0603C104M5RACTU | KEMET
kleinvoet | R51 | 47 | Resistor_SMD:R_0603_1608Metric_Pad0.98x0.95mm_HandSolder | ~ | ERJ-3EKF47R0V | Panasonic
kleinvoet | R52 | 47 | Resistor_SMD:R_0603_1608Metric_Pad0.98x0.95mm_HandSolder | ~ | ERJ-3EKF47R0V | Panasonic
kleinvoet | C76 | 10n | Capacitor_SMD:C_0603_1608Metric_Pad1.08x0.95mm_HandSolder | ~ | C0603C103J5RACTU | KEMET
kleinvoet | C78 | 10n | Capacitor_SMD:C_0603_1608Metric_Pad1.08x0.95mm_HandSolder | ~ | C0603C103J5RACTU | KEMET
kleinvoet | C71 | 100n | Capacitor_SMD:C_0603_1608Metric_Pad1.08x0.95mm_HandSolder | ~ | C0603C104M5RACTU | KEMET
kleinvoet | C74 | 100n | Capacitor_SMD:C_0603_1608Metric_Pad1.08x0.95mm_HandSolder | ~ | C0603C104M5RACTU | KEMET
kleinvoet | C18 | 220p | Capacitor_SMD:C_0603_1608Metric_Pad1.08x0.95mm_HandSolder | ~ | C0603C221J5GACTU | KEMET
kleinvoet | C19 | 220p | Capacitor_SMD:C_0603_1608Metric_Pad1.08x0.95mm_HandSolder | ~ | C0603C221J5GACTU | KEMET
kleinvoet | FB3 | 1k @ 100 MHz | Inductor_SMD:L_0603_1608Metric_Pad1.05x0.95mm_HandSolder | ~ | BLM18KG102SN1D | Murata Electronics
kleinvoet | FB4 | 1k @ 100 MHz | Inductor_SMD:L_0603_1608Metric_Pad1.05x0.95mm_HandSolder | ~ | BLM18KG102SN1D | Murata Electronics
kleinvoet | J3 | Sensor_Conn | grootvoet:TE_7-215079-8 | ~ | 7-215083-8 | TE Connectivity
kleinvoet | J3 | Sensor_Conn | grootvoet:TE_7-215079-8 | ~ | 7-215079-8 | TE Connectivity
kleinvoet | C30 | 220p | Capacitor_SMD:C_0603_1608Metric_Pad1.08x0.95mm_HandSolder | ~ | C0603C221J5GACTU | KEMET
kleinvoet | C31 | 220p | Capacitor_SMD:C_0603_1608Metric_Pad1.08x0.95mm_HandSolder | ~ | C0603C221J5GACTU | KEMET
kleinvoet | FB7 | 1k @ 100 MHz | Inductor_SMD:L_0603_1608Metric_Pad1.05x0.95mm_HandSolder | ~ | BLM18KG102SN1D | Murata Electronics
kleinvoet | FB11 | 1k @ 100 MHz | Inductor_SMD:L_0603_1608Metric_Pad1.05x0.95mm_HandSolder | ~ | BLM18KG102SN1D | Murata Electronics
kleinvoet | J6 | Sensor_Conn | grootvoet:TE_7-215079-8 | ~ | 7-215083-8 | TE Connectivity
kleinvoet | J6 | Sensor_Conn | grootvoet:TE_7-215079-8 | ~ | 7-215079-8 | TE Connectivity
kleinvoet | R84 | 100k | Resistor_SMD:R_0603_1608Metric_Pad0.98x0.95mm_HandSolder | ~ | RC0603FR-07100KL | Yageo
kleinvoet | Q1 | PMOS | Package_TO_SOT_SMD:SOT-23_Handsoldering | https://www.mouser.co.za/datasheet/2/308/NTR4101P-D-1814409.pdf | NTR3A30PZT1G | ON Semiconductor | Low Rds_on; Low Gate Voltage
kleinvoet | R86 | 10k | Resistor_SMD:R_0603_1608Metric_Pad0.98x0.95mm_HandSolder | ~ | RC0603JR-0710KL | Yageo
kleinvoet | C58 | 10u | Capacitor_SMD:C_0805_2012Metric_Pad1.18x1.45mm_HandSolder | ~ | C0805C106K9PACTU | KEMET
kleinvoet | CB38 | 10n | Capacitor_SMD:C_0603_1608Metric_Pad1.08x0.95mm_HandSolder | ~ | C0603C103J5RACTU | KEMET | C0G
kleinvoet | C63 | 10u | Capacitor_SMD:C_0805_2012Metric_Pad1.18x1.45mm_HandSolder | ~ | C0805C106K9PACTU | KEMET
kleinvoet | TP14 | VIN | TestPoint:TestPoint_Pad_D1.0mm | ~
kleinvoet | U8 | MCP73831-2-OT | Package_TO_SOT_SMD:SOT-23-5 | http://ww1.microchip.com/downloads/en/DeviceDoc/20001984g.pdf | MCP73831T-2ACI/OT | Microchip
kleinvoet | D6 | ORANGE | LED_SMD:LED_0603_1608Metric_Pad1.05x0.95mm_HandSolder | ~ | SML-D12D8WT86C | ROHM Semiconductor
kleinvoet | R87 | 2.2k | Resistor_SMD:R_0603_1608Metric_Pad0.98x0.95mm_HandSolder | ~ | RC0603FR-072K2L | Yageo
kleinvoet | R85 | 5.1k | Resistor_SMD:R_0603_1608Metric_Pad0.98x0.95mm_HandSolder | ~ | AC0603FR-135K1L | Yageo
kleinvoet | F1 | 400mA | Fuse:Fuse_0603_1608Metric_Pad1.05x0.95mm_HandSolder | ~ | 0ZCM0020FF2G | Bel Fuse
kleinvoet | FB8 | 100 @ 100 MHz | Inductor_SMD:L_0603_1608Metric_Pad1.05x0.95mm_HandSolder | ~ | BLM18EG101TZ1D | Murata Electronics
kleinvoet | D7 | RED | LED_SMD:LED_0603_1608Metric_Pad1.05x0.95mm_HandSolder | ~ | SML-D12U8WT86C | ROHM Semiconductor
kleinvoet | R88 | 2.2k | Resistor_SMD:R_0603_1608Metric_Pad0.98x0.95mm_HandSolder | ~ | RC0603FR-072K2L | Yageo
kleinvoet | BT1 | COIN_BAT | grootvoet:BatteryHolder_Keystone_3002_1x2032 | CR2032 | 2898 | Keystone Electronics
kleinvoet | C60 | 10u | Capacitor_SMD:C_0805_2012Metric_Pad1.18x1.45mm_HandSolder | ~ | C0805C106K9PACTU | KEMET
kleinvoet | C62 | 10u | Capacitor_SMD:C_0805_2012Metric_Pad1.18x1.45mm_HandSolder | ~ | C0805C106K9PACTU | KEMET
kleinvoet | D5 | Vf low | Diode_SMD:D_SOD-123 | ~ | RSX101MM-30TR | ROHM Semiconductor
kleinvoet | D4 | Vf low | Diode_SMD:D_SOD-123 | ~ | RSX101MM-30TR | ROHM Semiconductor
kleinvoet | U9 | TPS73733QDRBRQ1 | grootvoet:Texas_DRB0008A |  | TPS73733QDRBRQ1 | Texas Instruments
kleinvoet | C59 | 10u | Capacitor_SMD:C_0805_2012Metric_Pad1.18x1.45mm_HandSolder | ~ | C0805C106K9PACTU | KEMET
kleinvoet | J13 | USB_C_Receptacle_USB2.0 | grootvoet:USB_C_Recepetacle_JAE_DX07S016JA1 | https://www.usb.org/sites/default/files/documents/usb_type-c.zip | DX07S016JA1R1500 | JAE Electronics
kleinvoet | R90 | 5.1k | Resistor_SMD:R_0603_1608Metric_Pad0.98x0.95mm_HandSolder | ~ | AC0603FR-135K1L | Yageo
kleinvoet | R91 | 5.1k | Resistor_SMD:R_0603_1608Metric_Pad0.98x0.95mm_HandSolder | ~ | AC0603FR-135K1L | Yageo
kleinvoet | H3 | MountingHole_Pad | MountingHole:MountingHole_3.2mm_M3_Pad_Via | ~
kleinvoet | H2 | MountingHole_Pad | MountingHole:MountingHole_3.2mm_M3_Pad_Via | ~
kleinvoet | J12 | JST-PH | grootvoet:JST_PH_S2B-PH-SM4-TB_1x02-1MP_P2.00mm_Horizontal | ~ | 1769 | Adafruit
kleinvoet | U10 | USBLC6-2SC6 | grootvoet:SOT-666_Handsoldering | https://www.st.com/resource/en/datasheet/usblc6-2.pdf | USBLC6-2P6 | STMicroelectronics
kleinvoet | CB39 | 100n | Capacitor_SMD:C_0603_1608Metric_Pad1.08x0.95mm_HandSolder | ~ | C0603C104M5RACTU | KEMET
kleinvoet | R89 | 10k | Resistor_SMD:R_0603_1608Metric_Pad0.98x0.95mm_HandSolder | ~ | RC0603JR-0710KL | Yageo
kleinvoet | C3 | 1u | Capacitor_SMD:C_0603_1608Metric_Pad1.08x0.95mm_HandSolder | ~ | C0603C105K8RACTU | KEMET
kleinvoet | R65 | 100k | Resistor_SMD:R_0603_1608Metric_Pad0.98x0.95mm_HandSolder | ~ | RC0603FR-07100KL | Yageo
kleinvoet | JP8 | SD_DET_SEL | Jumper:SolderJumper-3_P1.3mm_Bridged12_RoundedPad1.0x1.5mm_NumberLabels | ~
kleinvoet | C66 | 1u | Capacitor_SMD:C_0603_1608Metric_Pad1.08x0.95mm_HandSolder | ~ | C0603C105K8RACTU | KEMET
kleinvoet | C64 | 10u | Capacitor_SMD:C_0805_2012Metric_Pad1.18x1.45mm_HandSolder | ~ | C0805C106K9PACTU | KEMET | Low ESR
kleinvoet | FB10 | BLM15HD102SN1 | Inductor_SMD:L_0402_1005Metric | ~ | BLM15HD102SN1D | Murata Electronics
kleinvoet | CB40 | 100n | Capacitor_SMD:C_0603_1608Metric_Pad1.08x0.95mm_HandSolder | ~ | C0603C104M5RACTU | KEMET
kleinvoet | H16 | MountingHole_Pad | MountingHole:MountingHole_3.2mm_M3_Pad_Via | ~
kleinvoet | H15 | MountingHole_Pad | MountingHole:MountingHole_3.2mm_M3_Pad_Via | ~
kleinvoet | H14 | MountingHole_Pad | MountingHole:MountingHole_3.2mm_M3_Pad_Via | ~
kleinvoet | H13 | MountingHole_Pad | MountingHole:MountingHole_3.2mm_M3_Pad_Via | ~
kleinvoet | C65 | 10u | Capacitor_SMD:C_0805_2012Metric_Pad1.18x1.45mm_HandSolder | ~ | C0805C106K9PACTU | KEMET | Low ESR
kleinvoet | J16 | GPS_Transmission_Conn | Connector_PinHeader_1.27mm:PinHeader_2x04_P1.27mm_Vertical | ~ | FTSH-104-01-F-D | Samtec
kleinvoet | J2 | FTDI_Conn | Connector_PinHeader_2.54mm:PinHeader_1x06_P2.54mm_Vertical | ~
kleinvoet | R3 | 2.2k | Resistor_SMD:R_0603_1608Metric_Pad0.98x0.95mm_HandSolder | ~ | RC0603FR-072K2L | Yageo
kleinvoet | D2 | GREEN | LED_SMD:LED_0603_1608Metric_Pad1.05x0.95mm_HandSolder | ~ | SMLD12EN1WT86 | ROHM Semiconductor
kleinvoet | R4 | 2.2k | Resistor_SMD:R_0603_1608Metric_Pad0.98x0.95mm_HandSolder | ~ | RC0603FR-072K2L | Yageo
kleinvoet | D3 | YELLOW | LED_SMD:LED_0603_1608Metric_Pad1.05x0.95mm_HandSolder | ~ | SML-D12Y8WT86C | ROHM Semiconductor
kleinvoet | J4 | GPS_Transmission_Conn | Connector_PinHeader_1.27mm:PinHeader_2x04_P1.27mm_Vertical | ~ | FTSH-104-01-F-D | Samtec
kleinvoet | R20 | 47 | Resistor_SMD:R_0603_1608Metric_Pad0.98x0.95mm_HandSolder | ~ | ERJ-3EKF47R0V | Panasonic
Sensor_Board_1 | FB1 | 100 @ 100 MHz | Inductor_SMD:L_0603_1608Metric_Pad1.05x0.95mm_HandSolder | ~ | BLM18EG101TZ1D | Murata Electronics
Sensor_Board_1 | TP1 | TestPoint | TestPoint:TestPoint_Pad_D1.0mm | ~ | ICS-40300 | TDK InvenSense
Sensor_Board_1 | H2 | MountingHole | MountingHole:MountingHole_3.2mm_M3_Pad_Via | ~
Sensor_Board_1 | H1 | MountingHole | MountingHole:MountingHole_3.2mm_M3_Pad_Via | ~
Sensor_Board_1 | C2 | 10u | Capacitor_SMD:C_0805_2012Metric_Pad1.18x1.45mm_HandSolder | ~ | C0805C106K9PACTU | KEMET
Sensor_Board_1 | C1 | 1u | Capacitor_SMD:C_0603_1608Metric_Pad1.08x0.95mm_HandSolder | ~ | C0603C105K8RACTU | KEMET
Sensor_Board_1 | CB1 | 100n | Capacitor_SMD:C_0603_1608Metric_Pad1.08x0.95mm_HandSolder | ~ | C0603C104M5RACTU | KEMET
Sensor_Board_1 | C3 | 1u | Capacitor_SMD:C_0603_1608Metric_Pad1.08x0.95mm_HandSolder | ~ | C0603C105K8RACTU | KEMET
Sensor_Board_1 | CB3 | 100n | Capacitor_SMD:C_0603_1608Metric_Pad1.08x0.95mm_HandSolder | ~ | C0603C104M5RACTU | KEMET
Sensor_Board_1 | C10 | 47u | Capacitor_SMD:C_1206_3216Metric_Pad1.33x1.80mm_HandSolder | ~ | GRM31CR60J107KE39K | Murata Electronics | Specified 47u but that is min. (>47u is better)
Sensor_Board_1 | C11 | 47u | Capacitor_SMD:C_1206_3216Metric_Pad1.33x1.80mm_HandSolder | ~ | GRM31CR60J107KE39K | Murata Electronics | Specified 47u but that is min. (>47u is better)
Sensor_Board_1 | U1 | TLV741PxxDBVx | Package_TO_SOT_SMD:SOT-23-5 |  | TLV74118PDBVR | Texas Instruments
Sensor_Board_1 | D1 | RED | LED_SMD:LED_0603_1608Metric_Pad1.05x0.95mm_HandSolder | ~ | SML-D12U8WT86C | ROHM Semiconductor
Sensor_Board_1 | R21 | 2k2 | Resistor_SMD:R_0603_1608Metric_Pad0.98x0.95mm_HandSolder | ~ | ERJ-3EKF2201V | Panasonic
Sensor_Board_1 | J1 | Mic_Conn | grootvoet:TE_7-215079-8 | ~ | 7-215083-8 | TE Connectivity
Sensor_Board_1 | J1 | Mic_Conn | grootvoet:TE_7-215079-8 | ~ | 7-215079-8 | TE Connectivity
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

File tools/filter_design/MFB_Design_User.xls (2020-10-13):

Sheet: MFB Design
MFB Filter design spreadsheet
Michael Steffes |  | 2006-02-01
This spreadsheet takes the basic MFB 2nd order Low Pass design which needs an imbedded integrator to work
 | And solves for the component values with an view towards noise and loop gain control.
First we set up the design targets |  |  |  |  | Define some useful constants
 |  |  |  |  | And intermediate terms
DC Gain (Av) = |  | 2 | V/V |  | 4kT ===> | 1.6e-20 | Joules | T = 290K
Target Fo = |  | 1000000 | Hz |  | 2pi ===> | 6.283185307
Target Q = |  | 0.691 |  |  | 2kt/in^2 => | 1097.39369
 |  |  |  |  | (1+Av)/(1+3Av) | 0.4285714286
Now Select an amplifier from the table of Voltage Feedback Op Amps on the next sheet
Part # |  | GBW (MHz) | En (nV/rootHz) | Aol (V/V) | In(pA/rootHz)
OPA842 |  | 200 | 2.6 | 316227.766 | 2.7
Suggested R2 resistor to match noise for op amp.
R2 could be greater than this, but probably not too much to limit noise added at output.(total Eo computed below in cell F55)
Suggested R2 ==> |  | 316.20 | Ohms | This is solving for R2 noise less than op amp voltatge noise
 |  |  |  | assuming R3 = R2 as a starting point
Pick your R2 here ==> |  | 150 | ohms
Now compute some limits on setting the integrator pole at a targeted ratio above the Wo
Minimum value to get C1 non-negative |  |  |  | 2.073 | Must be greater than this for C1 > 0
Maximum value to get R3 = R2 |  |  |  | 3.455 | This will get R3=R2 for noise control
 |  |  |  |  | But may be causing noise gain peaking if the lower zero is below Fo
Now compute noise gain zero location for the R3=R2 solution
First compute the radical for the polynomial ===> |  |  |  | 0.7075678453
 |  | Lower zero location ====> |  | 716777.2379 | Hz
 |  | Upper zero location ====> |  | 4185400.765 | Hz
Enter the ratio of Integrator pole/wo =========> |  |  |  | 3.46 | Should be between the two numbers above (or higher if higher noise is ok)
Compute the inverse of this to use in calculations |  |  |  | 0.2894 |  | Estimated Phase Margin -----> |  |  | 62.53 | degrees
 |  |  |  |  |  | From the 2nd Sheet copy loop gain impact at Fmax
Suggested C2 value => |  | 3.071007103e-10 | F |  |  | Maximum signal Frequency --> |  |  | 1400000 | Hz
 | Now enter an actual value less than or equal to the suggested value |  |  |  |  | Loop gain at Maximum F -----> |  |  | 32.5 | dB
Enter actual C2 Value=> |  | 3.071007103e-10 | F | This cell copies the suggested value just above but can be overwritten.
Resulting Integrator pole location ===> |  |  |  | 3455000 | Hz
Here we compute the slight shift in targeted R1/R3 to account for finite loop gain effects
Adjustment factor to get Av ==> |  |  | 1.000009487 | This will normally be a number just barely over 1.0000000000
 |  |  |  | Would only be a meaningful adjustment for low Aol or high signal gain.
Actual target gain ==> |  | 2.000018974 | this is R1/R3
Now compute C1 to get solution ==> |  |  | 1.832934428e-09 | F
We can now compute R3 ===> |  |  | 149.998577 | ohms
And finally R1 then is given by > |  |  | 300 | ohms
Summarize Filter design here - |  |  | and recompute the filter achieved using the basic design equations
 |  |  | These should match the targets set at the top.
R1 ==> | 300 | ohms | DC Gain (Av) = |  | 2.000018974 | V/V
C1 ==> | 1.832934428e-09 | F | Actual Fo = |  | 1000000 | Hz
R2 ==> | 150 | ohms | Actual Q = |  | 0.691
C2 ==> | 3.071007103e-10 | F | Total Eo = |  | 10.047 | nV/rootHz | In passband
R3 ==> | 149.998577 | ohms | Input Referred noise at R3 |  | 5.023 | nV/rootHz

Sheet: PartSelection&NoiseGainPlots
This Sheet Plots the Open Loop gain and phase with the MFB noise gain |  |  |  |  |  |  |  |  |  | AMPLIFIER SELECTION TABLE. ASCENDING GAIN BANDWIDTH PRODUCT
It also plots results loop gain |  |  |  |  |  |  |  |  |  | PART # | GainBandwidth | Input Voltage | Input Current | DC Open | Comments
 |  |  |  |  |  |  |  |  |  |  | Product (Mhz) | Noise (nV/rootHz) | Noise (pA/rootHz) | Loop Gain (V/V)
Part number selected for this design ---> |  |  |  | OPA842 |  |  |  |  |  | OPA131 | 4 | 15 | 0.02 | 316000 | Low Cost JFET Input +/-15V supply
 |  |  |  |  |  |  |  |  |  | OPA340 | 5.5 | 25 | 0.05 | 1000000 | 2.7V->5.5V low power CMOS
Map Design variables over from the Design page |  |  |  |  |  |  |  |  |  | OPA364 | 7 | 17 | 0.02 | 100000 | 1.8V ->5.5V low power CMOS
R1 ==> | 300 | ohms |  |  |  |  |  |  |  | OPA227 | 8 | 2.3 | 0.4 | 100000000 | +/-15V high DC precision
C1 ==> | 1.832934428e-09 | F |  |  |  |  |  |  |  | OPA627 | 16 | 4.5 | 0.02 | 1000000 | +/-15V high DC Precision
R2 ==> | 150 | ohms |  |  |  |  |  |  |  | OPA727 | 20 | 6 | 0.02 | 1000000 | 4V to 12V E-trim precision amplifier
C2 ==> | 3.071007103e-10 | F | 1+Ct/C2 is the high frequency noise gain - set Ct looking at C2 if needed. |  |  |  |  |  |  | OPA228 | 33 | 3 | 0.4 | 100000000 | +/-15V high DC Precision, de-compensated
R3 ==> | 149.998577 | ohms |  |  | Noise Gain Poles are same as Desired |  |  |  |  | OPA350 | 38 | 5 | 0.05 | 1260000 | 2.7V->5.5V high speed CMOS
Ct --> | 3e-12 | F | ENTER THIS CAPACITOR TO CONTROL PHASE MARGIN |  | Filter Shape; In terms of Wo and Q they are |  |  |  |  | OPA637 | 80 | 4.8 | 0.02 | 1000000 | +/-15V high DC Precision, de-compensated
Fmax --> | 1400000 | Hz | ENTER MAXIMUM SIGNAL FREQUENCY THROUGH FILTER |  | Wo ---> | 1000000 | Hz |  |  | OPA830 | 110 | 9.5 | 3.7 | 20900 | RR Output, Aol Gain and Phase for 1kohm load
 |  |  |  | TO REPORT LOOP GAIN AT Fmax | Q --> | 0.691 |  |  |  | OPA2613 | 125 | 1.8 | 1.7 | 70794.57844 | +5V to +/-6V dual, low noise
 |  |  |  |  | Computed Noise Gain Zeroes |  |  |  |  | OPA355 | 150 | 5.8 | 0.1 | 40000 | 2.7V->5.5V low distortion CMOS
 |  |  |  |  |  |  |  |  |  | THS4130 | 180 | 1.3 | 1 | 3550 | +/-15V FDA
 |  |  |  |  | Low Frequency Zero -> |  | 715307.8041 | Hz |  | OPA842 | 200 | 2.6 | 2.7 | 316227.766 | +/-5V very low distortion
 |  |  |  |  | High Frequency Zero-> |  | 4153451.065 | Hz |  | THS4631 | 210 | 7 | 0.02 | 10000 | +/-15V JFET Input
 |  |  |  |  |  |  |  |  |  | OPA2822 | 220 | 2 | 1.6 | 100000 | +5V to +/-6V low noise dual
 |  |  |  |  | Estimated Phase Margin |  |  | 62.53 | degrees | THS4031 | 220 | 1.6 | 1.2 | 89000 | +/-15V low noise
 |  |  |  |  |  |  |  |  |  | OPA656 | 230 | 7 | 0.02 | 1778.27941 | +/-5V JFET Input, Trimmed DC precision
 |  |  |  |  |  |  |  |  |  | OPA820 | 280 | 2.5 | 1.7 | 1995.262315 | +5V to +/-6V low noise
 |  |  |  |  |  |  |  |  |  | THS4502 | 280 | 6.8 | 1.7 | 562 | +/-5V FDA
 |  |  |  |  | Series 1 is the noise gain magnitude |  |  |  |  | OPA2614 | 290 | 1.8 | 1.7 | 70794.57844 | +5V to +/-6V dual, non-unity gain stable
 |  |  |  |  | Series 2 is the noise gain phase |  |  |  |  | OPA690 | 300 | 5.4 | 3.1 | 2820 | Unity gain stable, high slew rate
 |  |  |  |  | Series 3 is the amplifier open loop gain |  |  |  |  | THS4271 | 400 | 3 | 3 | 5600 | Very low distortion
 |  |  |  |  | Series 4 is the amplifier open loop phase |  |  |  |  | OPA843 | 800 | 2 | 2.8 | 316227.766 | +/-5V non-unity gain stable, very low distortion
 |  |  |  |  |  |  |  |  |  | OPA657 | 1600 | 4.8 | 0.02 | 3162 | JFET Input, Trimmed DC, Decomped
 |  |  |  |  |  |  |  |  |  | OPA846 | 1750 | 1.2 | 2.8 | 31600 | +/-5V non-unity gain stable low noise
 |  |  |  |  |  |  |  |  |  | THS4511 | 2000 | 2 | 1.5 | 1410 | 5V FDA
 |  |  |  |  |  |  |  |  |  | THS4508 | 3000 | 2.3 | 2.9 | 562 | 5V FDA
 |  |  |  |  |  |  |  |  |  | OPA847 | 3900 | 0.85 | 2.5 | 79400 | Non-unity gain stable, very low nosie
 |  |  |  |  | Loop Gain at Fmax -> |  | 32.5 | dB
 |  |  |  |  | The lower the loop gain in the signal band of interest
 |  |  |  |  | the lower the SFDR will be.

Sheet: NoiseGainCalcula
This sheet calculates and plots the noise gain for the filter circuit - neglecting any output loading or Zo effects.
This is the basic noise gain a first order analysis would be seeing. Will compare to the one with Output loading and Zo to see if
 | only the integrator portion can be considered successfully in that later analysis.
Map Design variables over from the Design page
 |  |  |  | Intermediate Calculations |  |  | Constants
R1 ==> | 300 | ohms |  | R1||R2 | R1||R3 |  | 2*Pi = | 6.283185307
C1 ==> | 1.832934428e-09 | F |  | 100 | 99.99936754 |  | 180/Pi = | 57.29577951
R2 ==> | 150 | ohms
C2 ==> | 3.071007103e-10 | F
R3 ==> | 149.998577 | ohms
Ct --> | 3e-12 | F | Ct is added as either a parasitic value or a tuning value to control phase margin seperately from the filter characteristic.
 |  |  |  | This is entered in the NoiseGainPlots worksheet
Now we need to compute the polynomial coefficients for both numerator and denominator shown to right.
Scalar | 0.9903257235 | This is the high frequency beta due to capacitive divider.
Coefficients for the 2nd order zero equation |  |  |  |  |  |  | I believe these are the same as the filter target poles
 | B0 | B1 | B2 |  | Real | Imag | Wo --> | 6283185.307 | Rad | Find Cell Location of Loop Gain Xover
 | 3.94784176e+13 | 9092922.07 | 1 |  | -4546461.035 | 4336831.754 | Wo --> | 1000000 | Hz |  |  | 525
Compute radical --> |  | -0.9099095047 | B/2 term-> | 4546461.035 | -4546461.035 | -4336831.754 | Q --> | 0.6909973778 |  | Phase margin ----> |  | 62.52783621 | degrees
Coefficents for the 2nd order pole equation |  |  |  |  |  |  |  |  |  | Find Cell Location of Max. Frequency
 | B0 | B1 | B2 |  | Real | Imag | poles(Hz) |  |  |  |  | 315
 | 1.172902192e+14 | 30591314.19 | 1 |  | -26096902.71 | 0 | -4153451.065 | Amplifier Gain and phase |  | Loop Gain at Max. F |  | 32.47496566 | dB
Compute radical --> |  | 0.4986678917 | B/2 term-> | 15295657.1 | -4494411.485 | 0 | -715307.8041 | OPA842
 |  |  |  | Phase | Now set up for plotting noise gain and amplifer Aol gain and phase |  |  |  |  |  |  | Data point
Freq(Hz) | Freq(rad | Mag(dB) | Angle (deg) | Complex | Freq(Hz) | Noise gain |  | Amplifier Aol |  | Xover Frequency find |  | from table | Compute
 |  |  |  | Argument |  | Gain (dB) | Phase (deg) | Gain (dB) | Phase (deg) | and Phase margin |  |  | Loop Gain
1000 | 6283.185307 | -9.542488359 | -0.01 | 3.947837813e+13 | 1000 | 9.54 | 0.01 | 104.7 | -69.07 | 0 | 0 | 1 | 95.15751164
1023.292992 | 6429.539494 | -9.542488751 | -0.01 | 3.947837627e+13 | 1023.292992 | 9.54 | 0.01 | 104.5 | -69.5 | 0 | 0 | 2 | 94.95751125
1047.128548 | 6579.302708 | -9.542489162 | -0.01 | 3.947837432e+13 | 1047.128548 | 9.54 | 0.01 | 104.3 | -69.93 | 0 | 0 | 3 | 94.75751084
1071.519305 | 6732.554355 | -9.542489593 | -0.01 | 3.947837228e+13 | 1071.519305 | 9.54 | 0.01 | 104.1 | -70.35 | 0 | 0 | 4 | 94.55751041
1096.478196 | 6889.375692 | -9.542490044 | -0.01 | 3.947837014e+13 | 1096.478196 | 9.54 | 0.01 | 104 | -70.77 | 0 | 0 | 5 | 94.45750996
1122.018454 | 7049.849866 | -9.542490516 | -0.01 | 3.94783679e+13 | 1122.018454 | 9.54 | 0.01 | 103.8 | -71.17 | 0 | 0 | 6 | 94.25750948
1148.153621 | 7214.061965 | -9.54249101 | -0.01 | 3.947836556e+13 | 1148.153621 | 9.54 | 0.01 | 103.6 | -71.57 | 0 | 0 | 7 | 94.05750899
1174.897555 | 7382.099055 | -9.542491527 | -0.01 | 3.947836311e+13 | 1174.897555 | 9.54 | 0.01 | 103.4 | -71.97 | 0 | 0 | 8 | 93.85750847
1202.264435 | 7554.050231 | -9.542492069 | -0.01 | 3.947836054e+13 | 1202.264435 | 9.54 | 0.01 | 103.2 | -72.35 | 0 | 0 | 9 | 93.65750793
1230.268771 | 7730.006665 | -9.542492637 | -0.01 | 3.947835785e+13 | 1230.268771 | 9.54 | 0.01 | 103.1 | -72.73 | 0 | 0 | 10 | 93.55750736
1258.925412 | 7910.06165 | -9.542493231 | -0.01 | 3.947835504e+13 | 1258.925412 | 9.54 | 0.01 | 102.9 | -73.1 | 0 | 0 | 11 | 93.35750677
1288.249552 | 8094.310655 | -9.542493853 | -0.01 | 3.947835209e+13 | 1288.249552 | 9.54 | 0.01 | 102.7 | -73.46 | 0 | 0 | 12 | 93.15750615
1318.256739 | 8282.851371 | -9.542494505 | -0.01 | 3.9478349e+13 | 1318.256739 | 9.54 | 0.01 | 102.5 | -73.82 | 0 | 0 | 13 | 92.9575055
1348.962883 | 8475.783764 | -9.542495187 | -0.01 | 3.947834577e+13 | 1348.962883 | 9.54 | 0.01 | 102.3 | -74.17 | 0 | 0 | 14 | 92.75750481
1380.384265 | 8673.21013 | -9.542495901 | -0.02 | 3.947834238e+13 | 1380.384265 | 9.54 | 0.02 | 102.1 | -74.51 | 0 | 0 | 15 | 92.5575041
1412.537545 | 8875.235146 | -9.542496649 | -0.02 | 3.947833883e+13 | 1412.537545 | 9.54 | 0.02 | 101.9 | -74.85 | 0 | 0 | 16 | 92.35750335
1445.439771 | 9081.96593 | -9.542497433 | -0.02 | 3.947833512e+13 | 1445.439771 | 9.54 | 0.02 | 101.8 | -75.18 | 0 | 0 | 17 | 92.25750257
1479.108388 | 9293.512092 | -9.542498253 | -0.02 | 3.947833123e+13 | 1479.108388 | 9.54 | 0.02 | 101.6 | -75.5 | 0 | 0 | 18 | 92.05750175
1513.561248 | 9509.985798 | -9.542499112 | -0.02 | 3.947832716e+13 | 1513.561248 | 9.54 | 0.02 | 101.4 | -75.82 | 0 | 0 | 19 | 91.85750089
1548.816619 | 9731.501823 | -9.542500011 | -0.02 | 3.94783229e+13 | 1548.816619 | 9.54 | 0.02 | 101.2 | -76.13 | 0 | 0 | 20 | 91.65749999
1584.893192 | 9958.17762 | -9.542500953 | -0.02 | 3.947831844e+13 | 1584.893192 | 9.54 | 0.02 | 101 | -76.43 | 0 | 0 | 21 | 91.45749905
1621.810097 | 10190.13337 | -9.542501939 | -0.02 | 3.947831377e+13 | 1621.810097 | 9.54 | 0.02 | 100.8 | -76.73 | 0 | 0 | 22 | 91.25749806
1659.586907 | 10427.49207 | -9.542502971 | -0.02 | 3.947830887e+13 | 1659.586907 | 9.54 | 0.02 | 100.6 | -77.02 | 0 | 0 | 23 | 91.05749703
1698.243652 | 10670.37957 | -9.542504053 | -0.02 | 3.947830375e+13 | 1698.243652 | 9.54 | 0.02 | 100.4 | -77.31 | 0 | 0 | 24 | 90.85749595
1737.800829 | 10918.92463 | -9.542505185 | -0.02 | 3.947829838e+13 | 1737.800829 | 9.54 | 0.02 | 100.3 | -77.59 | 0 | 0 | 25 | 90.75749482
1778.27941 | 11173.25906 | -9.54250637 | -0.02 | 3.947829276e+13 | 1778.27941 | 9.54 | 0.02 | 100.1 | -77.86 | 0 | 0 | 26 | 90.55749363
1819.700859 | 11433.5177 | -9.542507612 | -0.02 | 3.947828688e+13 | 1819.700859 | 9.54 | 0.02 | 99.87 | -78.13 | 0 | 0 | 27 | 90.32749239
1862.087137 | 11699.83854 | -9.542508912 | -0.02 | 3.947828072e+13 | 1862.087137 | 9.54 | 0.02 | 99.68 | -78.39 | 0 | 0 | 28 | 90.13749109
1905.460718 | 11972.36279 | -9.542510273 | -0.02 | 3.947827427e+13 | 1905.460718 | 9.54 | 0.02 | 99.48 | -78.65 | 0 | 0 | 29 | 89.93748973
1949.8446 | 12251.23494 | -9.542511698 | -0.02 | 3.947826751e+13 | 1949.8446 | 9.54 | 0.02 | 99.29 | -78.9 | 0 | 0 | 30 | 89.7474883
1995.262315 | 12536.60286 | -9.542513191 | -0.02 | 3.947826044e+13 | 1995.262315 | 9.54 | 0.02 | 99.1 | -79.15 | 0 | 0 | 31 | 89.55748681
2041.737945 | 12828.61786 | -9.542514754 | -0.02 | 3.947825303e+13 | 2041.737945 | 9.54 | 0.02 | 98.91 | -79.39 | 0 | 0 | 32 | 89.36748525
2089.296131 | 13127.43475 | -9.54251639 | -0.02 | 3.947824527e+13 | 2089.296131 | 9.54 | 0.02 | 98.71 | -79.62 | 0 | 0 | 33 | 89.16748361
2137.96209 | 13433.21199 | -9.542518104 | -0.02 | 3.947823715e+13 | 2137.96209 | 9.54 | 0.02 | 98.52 | -79.86 | 0 | 0 | 34 | 88.9774819
2187.761624 | 13746.11169 | -9.542519898 | -0.02 | 3.947822865e+13 | 2187.761624 | 9.54 | 0.02 | 98.33 | -80.08 | 0 | 0 | 35 | 88.7874801
2238.721139 | 14066.29976 | -9.542521777 | -0.02 | 3.947821974e+13 | 2238.721139 | 9.54 | 0.02 | 98.13 | -80.3 | 0 | 0 | 36 | 88.58747822
2290.867653 | 14393.94598 | -9.542523745 | -0.03 | 3.947821042e+13 | 2290.867653 | 9.54 | 0.03 | 97.94 | -80.52 | 0 | 0 | 37 | 88.39747626
2344.228815 | 14729.22405 | -9.542525805 | -0.03 | 3.947820065e+13 | 2344.228815 | 9.54 | 0.03 | 97.74 | -80.73 | 0 | 0 | 38 | 88.1974742
2398.832919 | 15072.31175 | -9.542527962 | -0.03 | 3.947819043e+13 | 2398.832919 | 9.54 | 0.03 | 97.55 | -80.94 | 0 | 0 | 39 | 88.00747204
2454.708916 | 15423.39099 | -9.542530221 | -0.03 | 3.947817972e+13 | 2454.708916 | 9.54 | 0.03 | 97.35 | -81.14 | 0 | 0 | 40 | 87.80746978
2511.886432 | 15782.64792 | -9.542532587 | -0.03 | 3.947816851e+13 | 2511.886432 | 9.54 | 0.03 | 97.16 | -81.34 | 0 | 0 | 41 | 87.61746741
2570.395783 | 16150.27302 | -9.542535063 | -0.03 | 3.947815677e+13 | 2570.395783 | 9.54 | 0.03 | 96.96 | -81.54 | 0 | 0 | 42 | 87.41746494
2630.267992 | 16526.4612 | -9.542537657 | -0.03 | 3.947814448e+13 | 2630.267992 | 9.54 | 0.03 | 96.76 | -81.73 | 0 | 0 | 43 | 87.21746234
2691.534804 | 16911.41193 | -9.542540373 | -0.03 | 3.947813161e+13 | 2691.534804 | 9.54 | 0.03 | 96.57 | -81.91 | 0 | 0 | 44 | 87.02745963
2754.228703 | 17305.32932 | -9.542543217 | -0.03 | 3.947811813e+13 | 2754.228703 | 9.54 | 0.03 | 96.37 | -82.09 | 0 | 0 | 45 | 86.82745678
2818.382931 | 17708.42222 | -9.542546195 | -0.03 | 3.947810402e+13 | 2818.382931 | 9.54 | 0.03 | 96.18 | -82.27 | 0 | 0 | 46 | 86.63745381
2884.031503 | 18120.90437 | -9.542549313 | -0.03 | 3.947808924e+13 | 2884.031503 | 9.54 | 0.03 | 95.98 | -82.44 | 0 | 0 | 47 | 86.43745069
2951.209227 | 18542.99445 | -9.542552578 | -0.03 | 3.947807376e+13 | 2951.209227 | 9.54 | 0.03 | 95.78 | -82.62 | 0 | 0 | 48 | 86.23744742
3019.95172 | 18974.91628 | -9.542555997 | -0.03 | 3.947805756e+13 | 3019.95172 | 9.54 | 0.03 | 95.59 | -82.78 | 0 | 0 | 49 | 86.047444
3090.295433 | 19416.89886 | -9.542559578 | -0.03 | 3.947804059e+13 | 3090.295433 | 9.54 | 0.03 | 95.39 | -82.94 | 0 | 0 | 50 | 85.84744042
3162.27766 | 19869.17653 | -9.542563327 | -0.03 | 3.947802282e+13 | 3162.27766 | 9.54 | 0.03 | 95.19 | -83.1 | 0 | 0 | 51 | 85.64743667
3235.936569 | 20331.98911 | -9.542567252 | -0.04 | 3.947800421e+13 | 3235.936569 | 9.54 | 0.04 | 95 | -83.26 | 0 | 0 | 52 | 85.45743275
3311.311215 | 20805.58197 | -9.542571363 | -0.04 | 3.947798473e+13 | 3311.311215 | 9.54 | 0.04 | 94.8 | -83.41 | 0 | 0 | 53 | 85.25742864
3388.441561 | 21290.20623 | -9.542575667 | -0.04 | 3.947796433e+13 | 3388.441561 | 9.54 | 0.04 | 94.6 | -83.56 | 0 | 0 | 54 | 85.05742433
3467.368505 | 21786.11884 | -9.542580175 | -0.04 | 3.947794297e+13 | 3467.368505 | 9.54 | 0.04 | 94.4 | -83.7 | 0 | 0 | 55 | 84.85741983
3548.133892 | 22293.58274 | -9.542584894 | -0.04 | 3.94779206e+13 | 3548.133892 | 9.54 | 0.04 | 94.21 | -83.85 | 0 | 0 | 56 | 84.66741511
3630.780548 | 22812.86699 | -9.542589836 | -0.04 | 3.947789718e+13 | 3630.780548 | 9.54 | 0.04 | 94.01 | -83.99 | 0 | 0 | 57 | 84.46741016
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

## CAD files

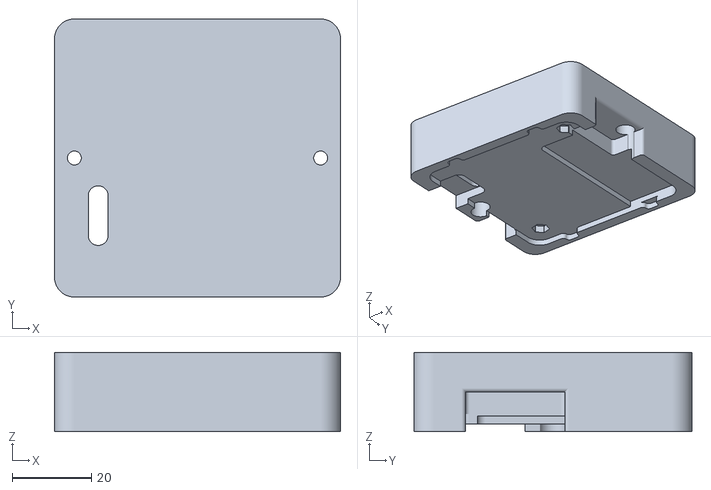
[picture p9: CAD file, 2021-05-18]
cad/Main_holder.stl
72.0 x 70.0 x 20.0

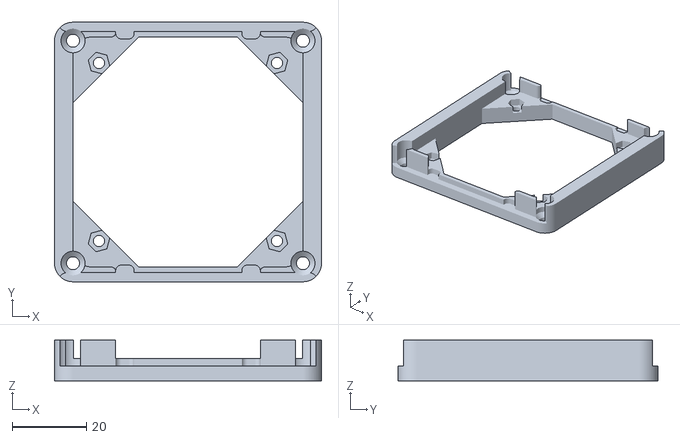
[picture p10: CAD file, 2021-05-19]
cad/GPS_holder.stl
72.0 x 70.0 x 11.0

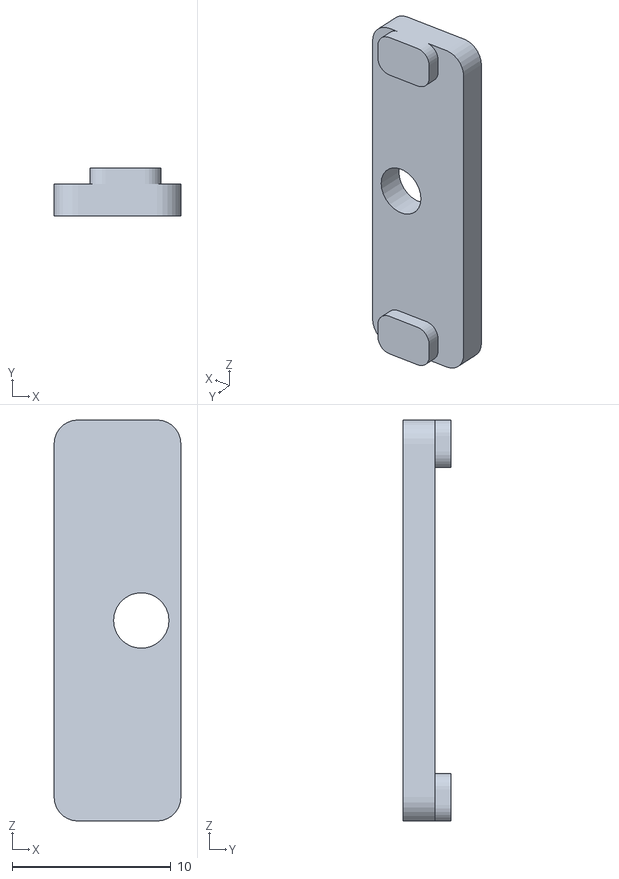
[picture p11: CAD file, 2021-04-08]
cad/Sensorboard_spacer.stl
8.00 x 3.00 x 25.3

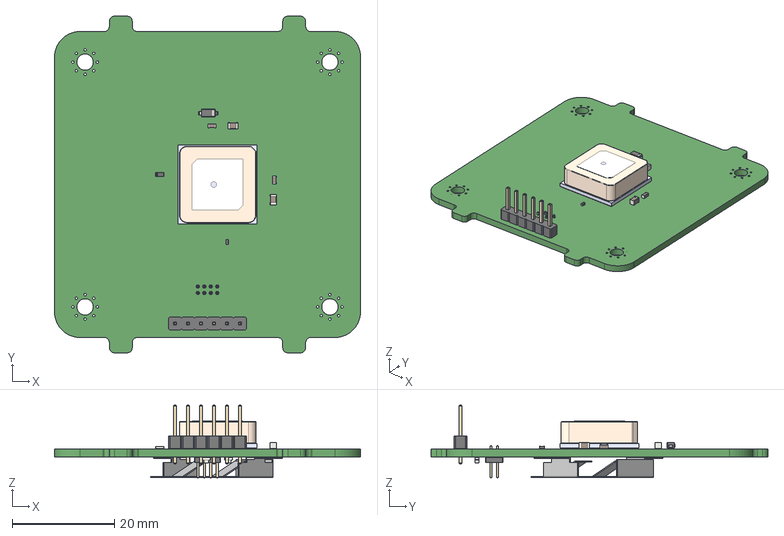
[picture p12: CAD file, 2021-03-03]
cad/kleinvoet_gps.step
60.0 x 66.0 x 14.2 mm

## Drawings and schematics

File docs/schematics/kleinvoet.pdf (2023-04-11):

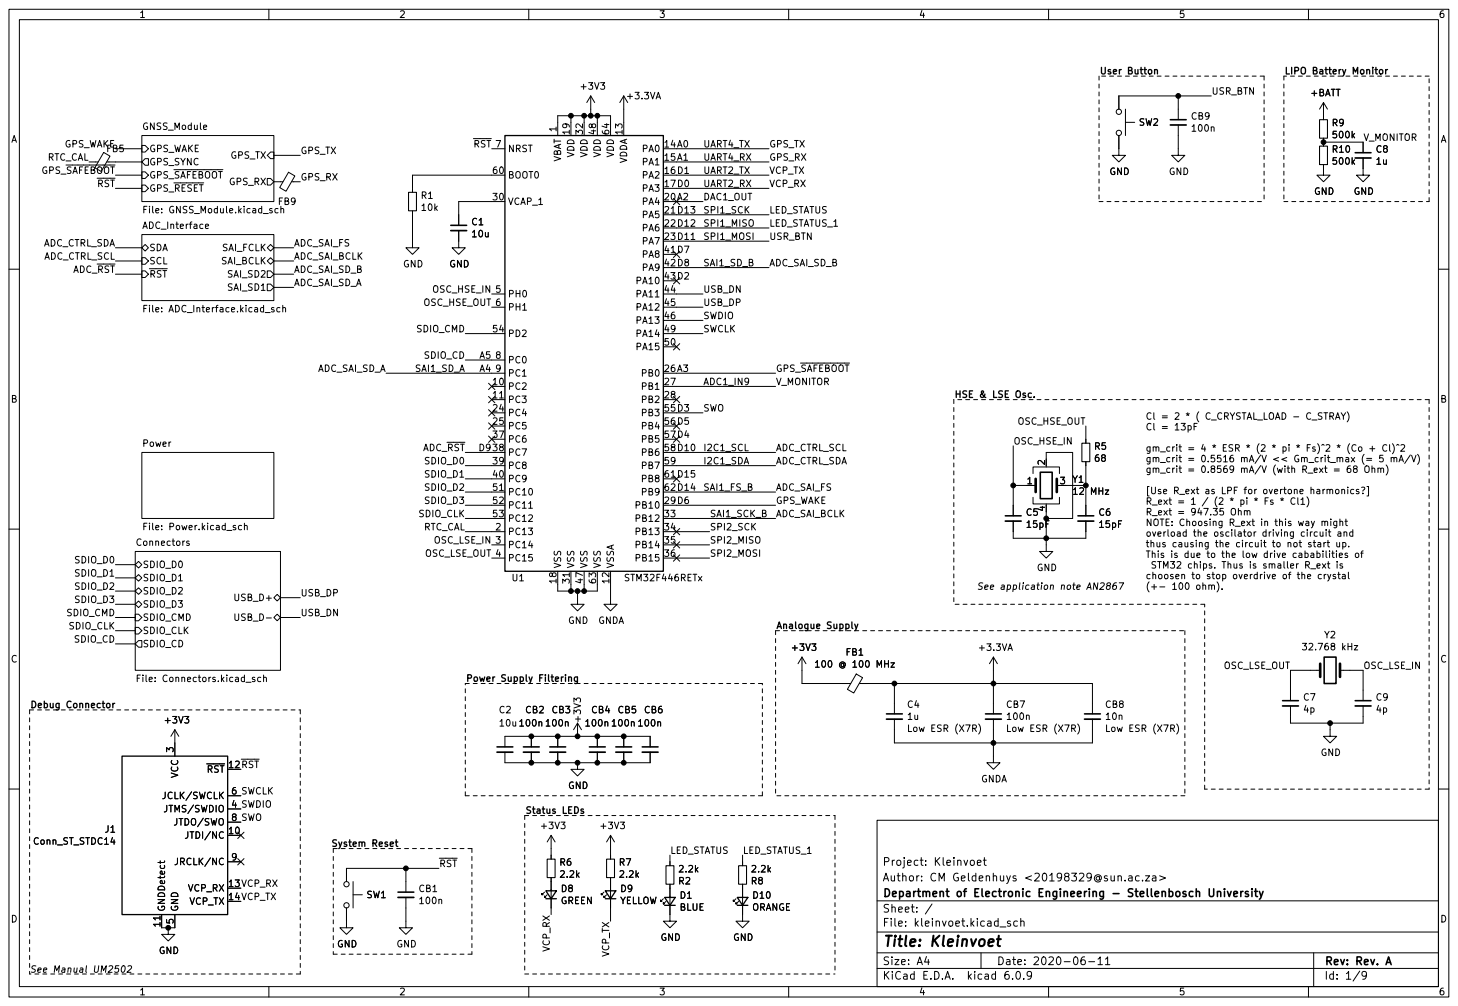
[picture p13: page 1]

1 PC2 10 PC3 11 VSSA 12 VDDA 13 PA0 14 PA1 15 PA2 16 PA3 17 VSS 18 VDD 19 PC13 2 PA4 20 PA5 21 PA6 22 PA7 23 PC4 24 PC5 25 PB0 26 PB1 27 PB2 28 PB10 29 PC14 3 VCAP_1 30 VSS 31 VDD 32 PB12 33 PB13 34 PB14 35 PB15 36 PC6 37 PC7 38 PC8 39 PC15 4 PC9 40 PA8 41 PA9 42 PA10 43 PA11 44 PA12 45 PA13 46 VSS 47 VDD 48 PA14 49 PH0 5 PA15 50 PC10 51 PC11 52 PC12 53 PD2 54 PB3 55 PB4 56 PB5 57 PB6 58 PB7 59 PH1 6 BOOT0 60 PB8 61 PB9 62 VSS 63 VDD 64 NRST 7 PC0 8 PC1 9 U1 STM32F446RETx GND

(+- 100 ohm). HSE & LSE Osc. See application note AN2867

gm_crit = 4 * ESR * (2 * pi * Fs)^2 * (Co + Cl)^2
gm_crit = 0.5516 mA/V << Gm_crit_max (= 5 mA/V)
gm_crit = 0.8569 mA/V (with R_ext = 68 Ohm)

[Use R_ext as LPF for overtone harmonics?]
R_ext = 1 / (2 * pi * Fs * Cl1) R_ext = 947.35 Ohm

NOTE: Choosing R_ext in this way might
overload the oscilator driving circuit and
thus causing the circuit to not start up. This is due to the low drive cababilities of

STM32 chips. Thus is smaller R_ext is
choosen to stop overdrive of the crystal

Author: CM Geldenhuys <20198329@sun.ac.za>
File: kleinvoet.kicad_sch Sheet: / Department of Electronic Engineering - Stellenbosch University

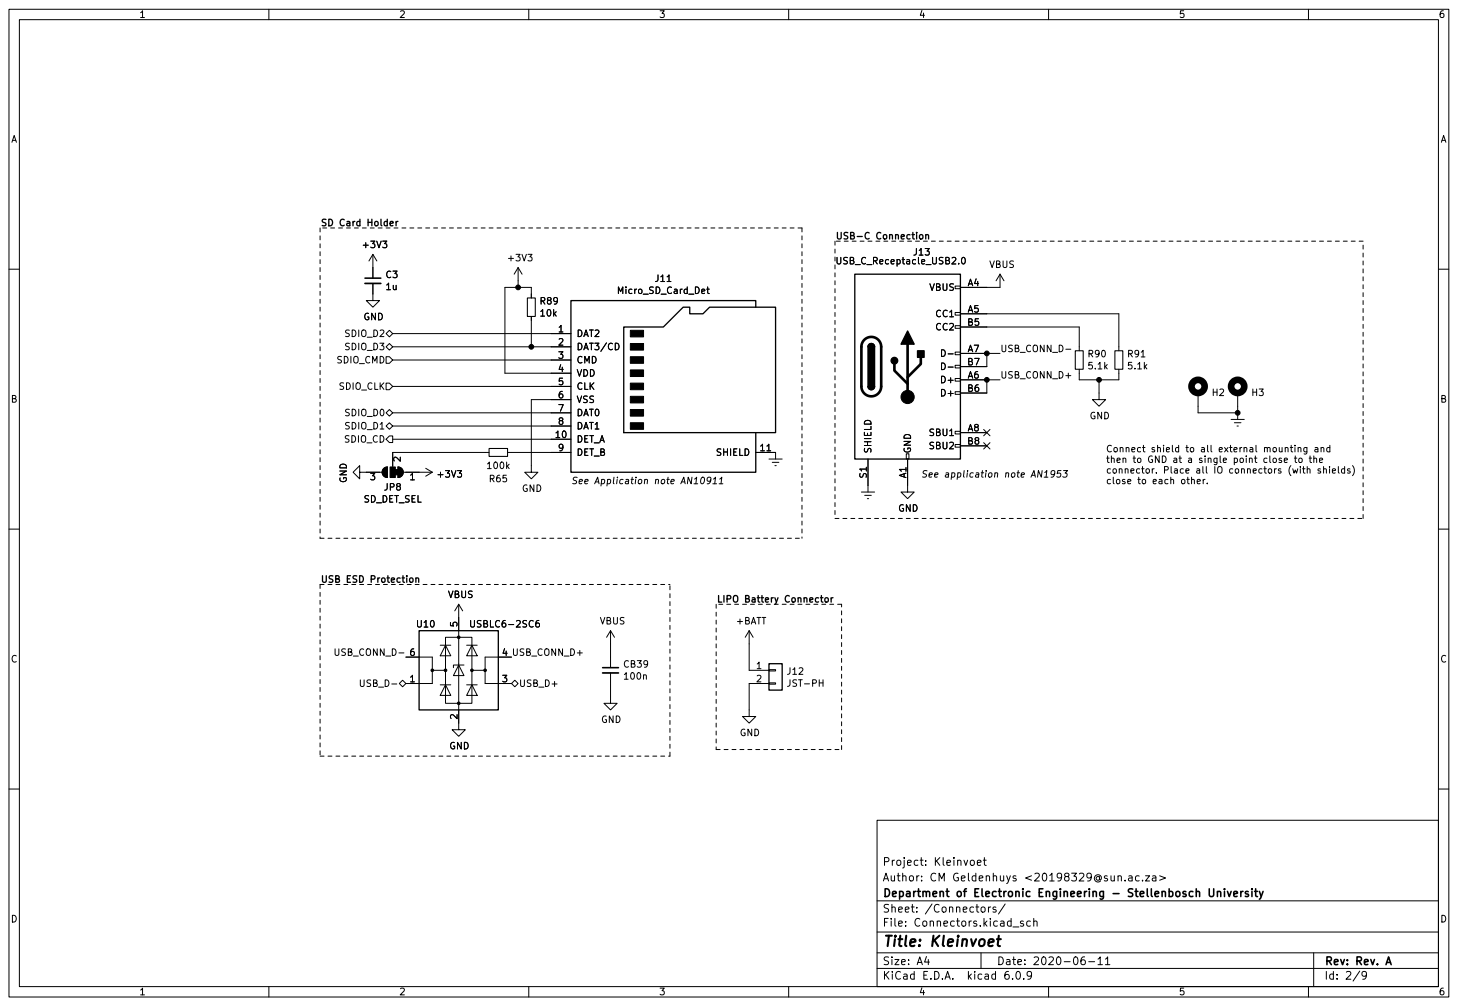
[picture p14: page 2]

Connect shield to all external mounting and
then to GND at a single point close to the

Project: Kleinvoet
Author: CM Geldenhuys <20198329@sun.ac.za>
File: Connectors.kicad_sch Sheet: /Connectors/ Department of Electronic Engineering - Stellenbosch University

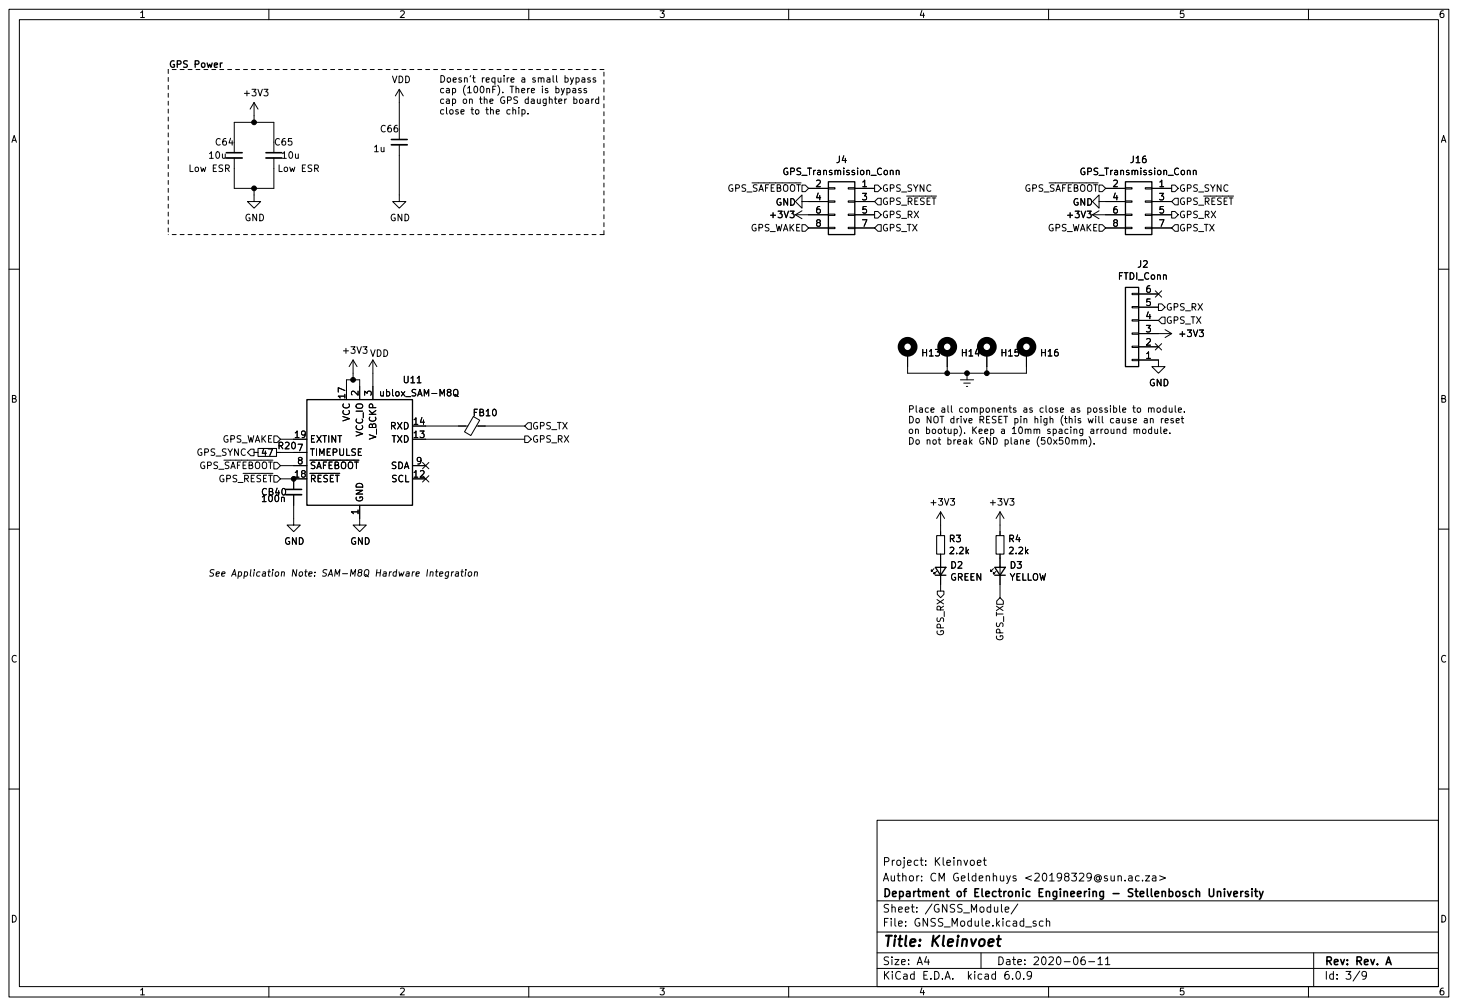
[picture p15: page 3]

Doesn't require a small bypass
cap (100nF). There is bypass
cap on the GPS daughter board
close to the chip.

1 SCL 12 TXD 13 RXD VCC 14 17

Do not break GND plane (50x50mm). U11
ublox_SAM-M8Q

Place all components as close as possible to module.
Do NOT drive RESET pin high (this will cause an reset
on bootup). Keep a 10mm spacing arround module.

Author: CM Geldenhuys <20198329@sun.ac.za>
Department of Electronic Engineering - Stellenbosch University
Sheet: /GNSS_Module/
File: GNSS_Module.kicad_sch
Id: 3/9 Title: Kleinvoet

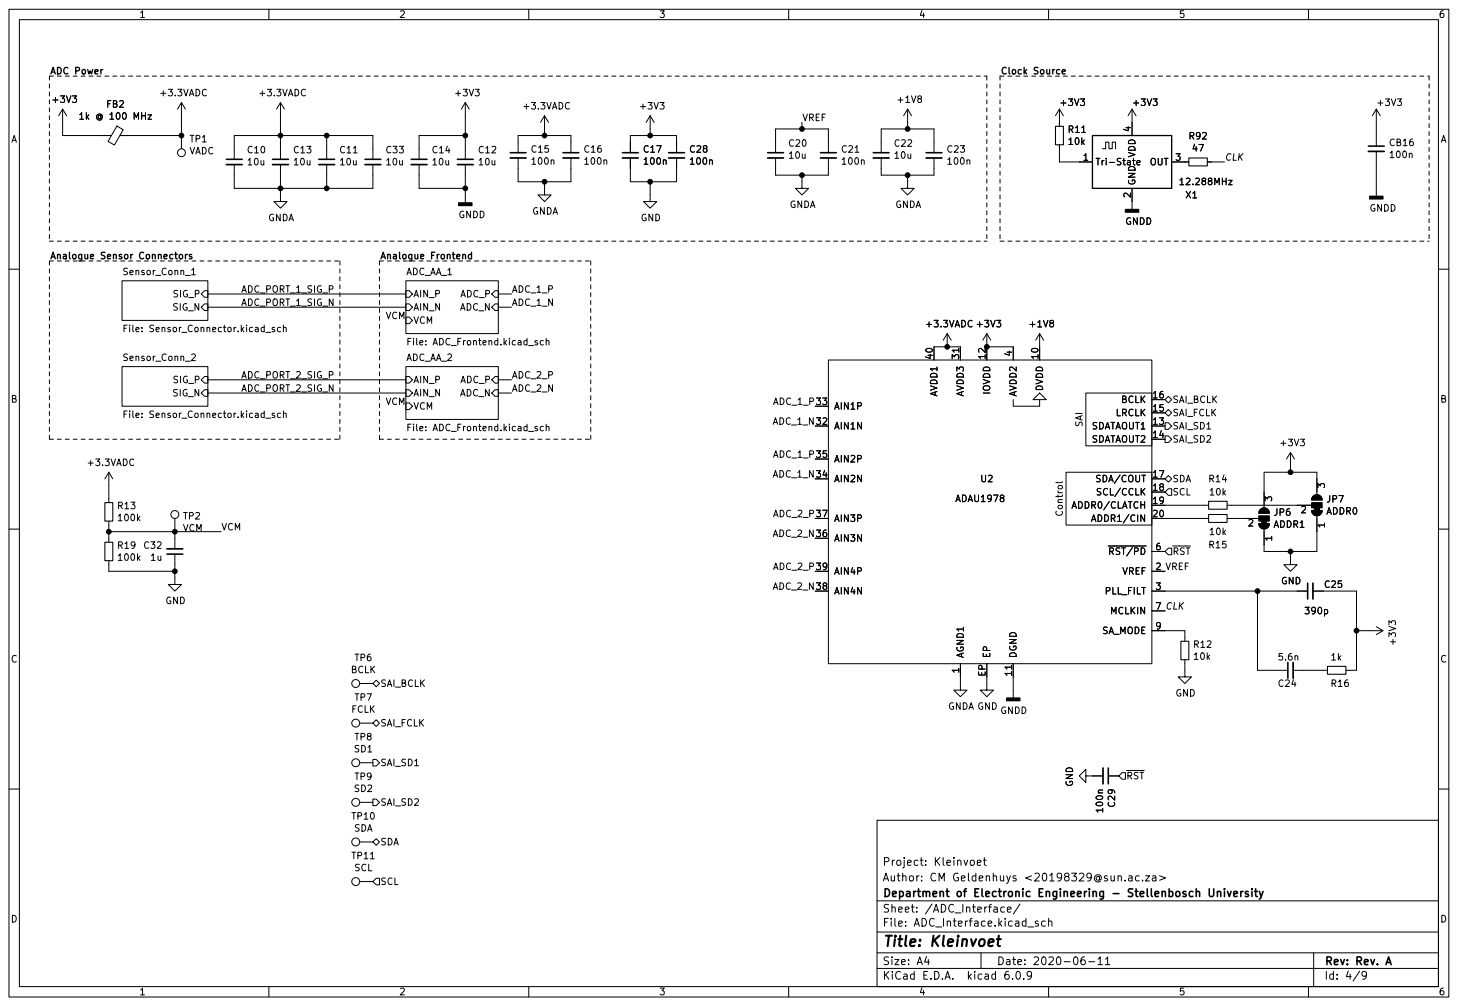
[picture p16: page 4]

Project: Kleinvoet
Author: CM Geldenhuys <20198329@sun.ac.za>
Department of Electronic Engineering - Stellenbosch University
Sheet: /ADC_Interface/
File: ADC_Interface.kicad_sch
Id: 4/9 Title: Kleinvoet

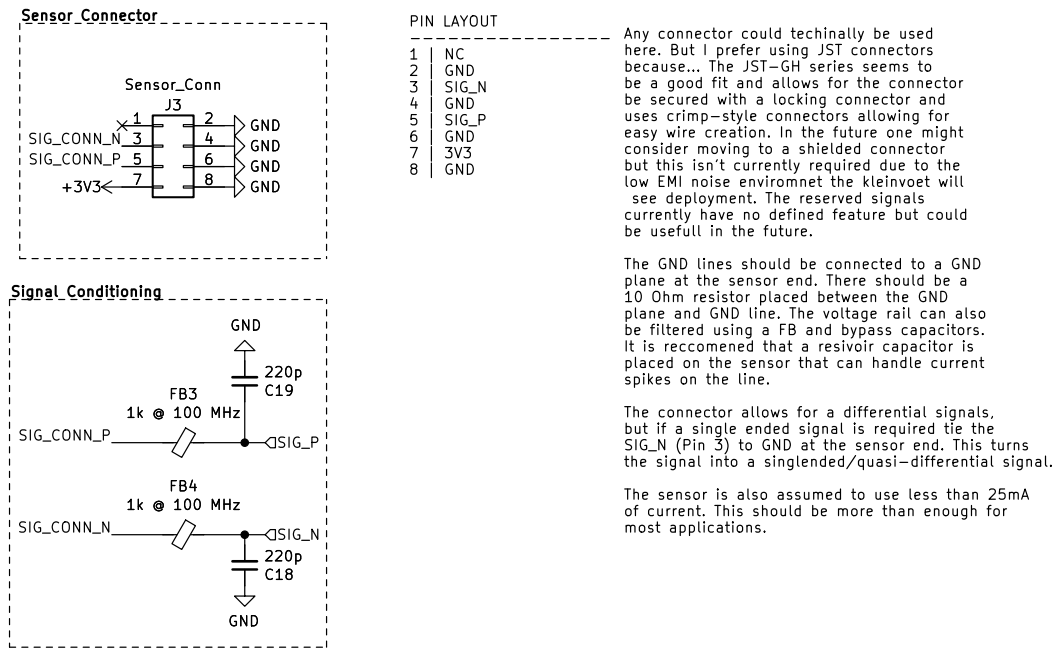
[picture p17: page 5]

Any connector could techinally be used
here. But I prefer using JST connectors because... The JST-GH series seems to be a good fit and allows for the connector

be secured with a locking connector and
uses crimp-style connectors allowing for
easy wire creation. In the future one might
consider moving to a shielded connector
but this isn't currently required due to the
low EMI noise enviromnet the kleinvoet will see deployment. The reserved signals

currently have no defined feature but could be usefull in the future. The GND lines should be connected to a GND

plane at the sensor end. There should be a
10 Ohm resistor placed between the GND
plane and GND line. The voltage rail can also
be filtered using a FB and bypass capacitors.
It is reccomened that a resivoir capacitor is
placed on the sensor that can handle current
spikes on the line.

The connector allows for a differential signals,
but if a single ended signal is required tie the
SIG_N (Pin 3) to GND at the sensor end. This turns
the signal into a singlended/quasi-differential signal. The sensor is also assumed to use less than 25mA of current. This should be more than enough for

Project: Kleinvoet
Author: CM Geldenhuys <20198329@sun.ac.za>
Department of Electronic Engineering - Stellenbosch University
Sheet: /ADC_Interface/Sensor_Conn_1/
File: Sensor_Connector.kicad_sch
Id: 5/9 Title: Kleinvoet

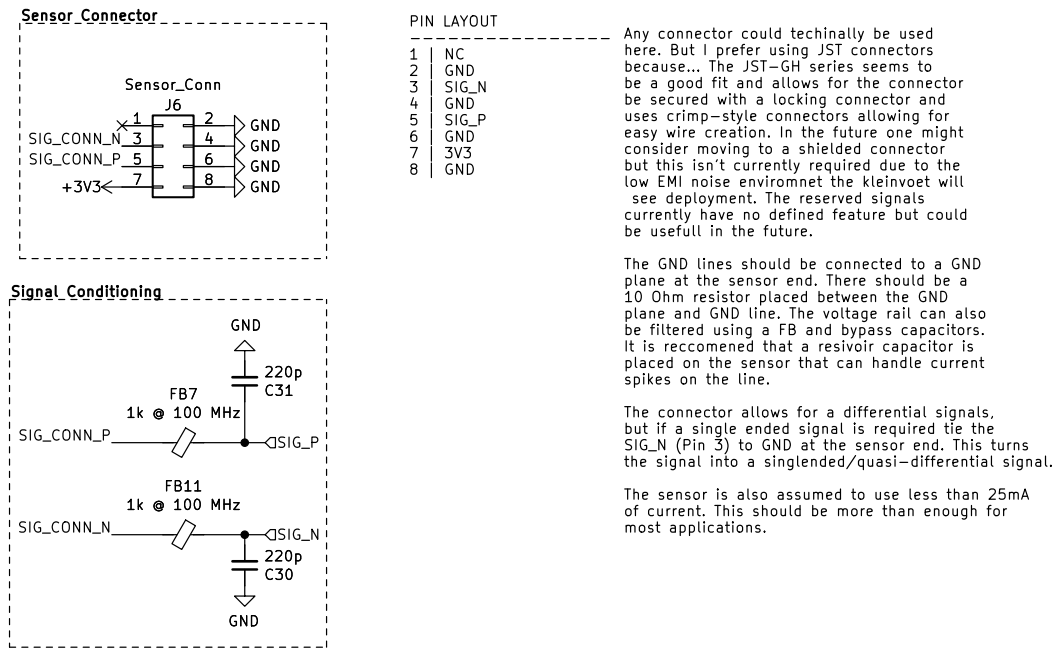
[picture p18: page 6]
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

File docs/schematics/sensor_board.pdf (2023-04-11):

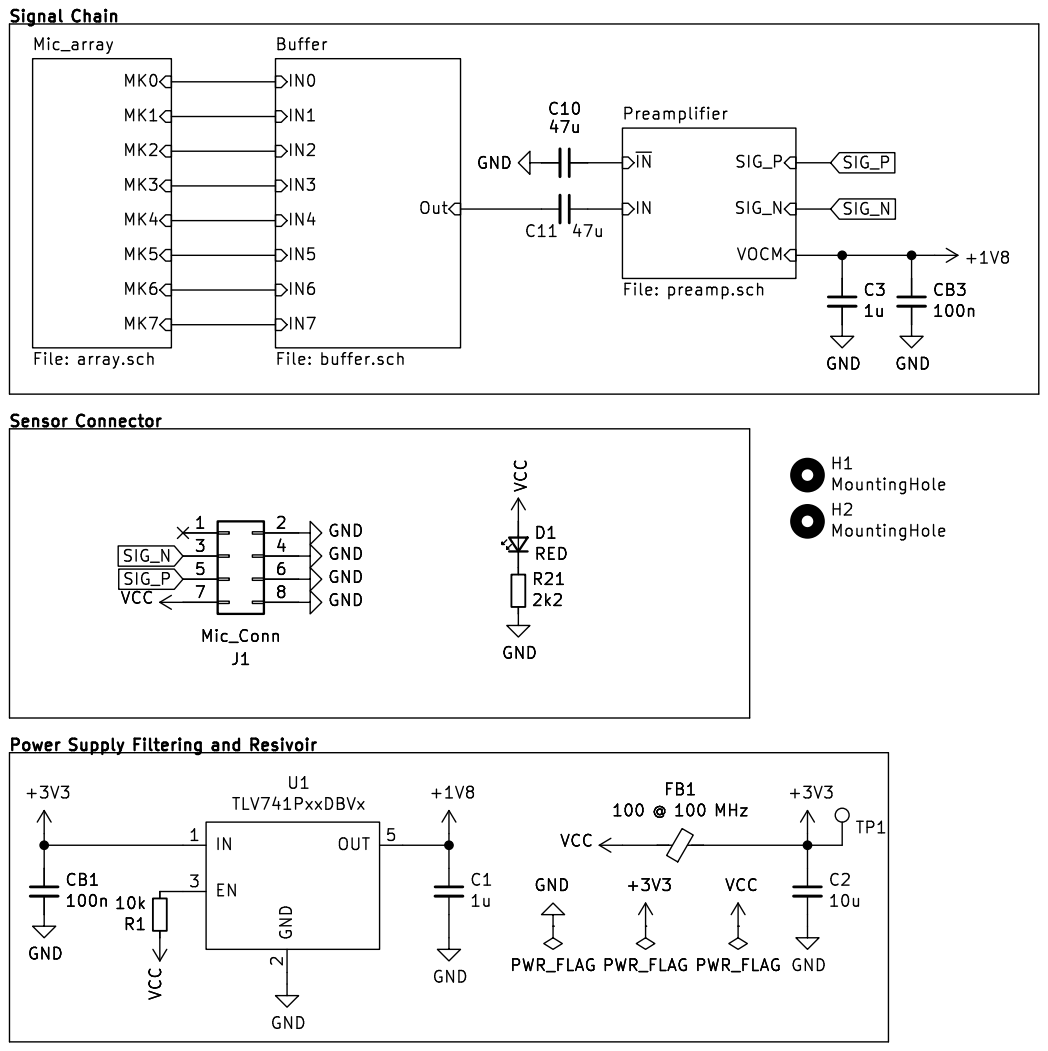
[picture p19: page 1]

2k2 GND GND GND GND

File: Sensor_Board.sch Sheet: / CM Geldenhuys

Id: 1/4 Title: Microphone Board

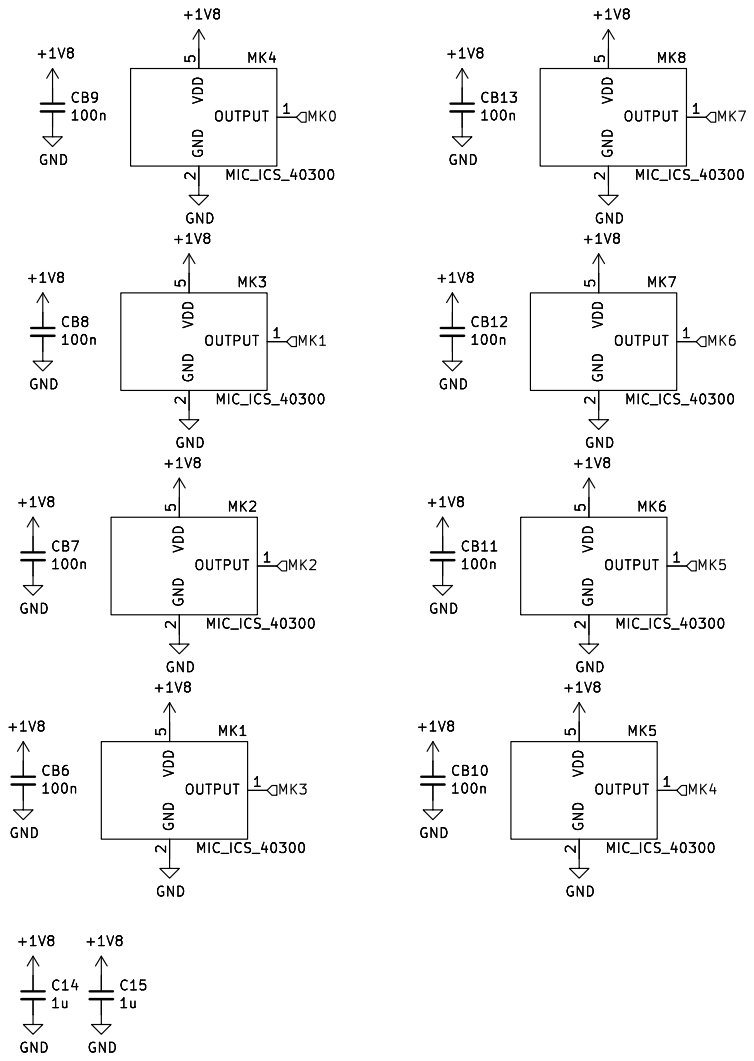
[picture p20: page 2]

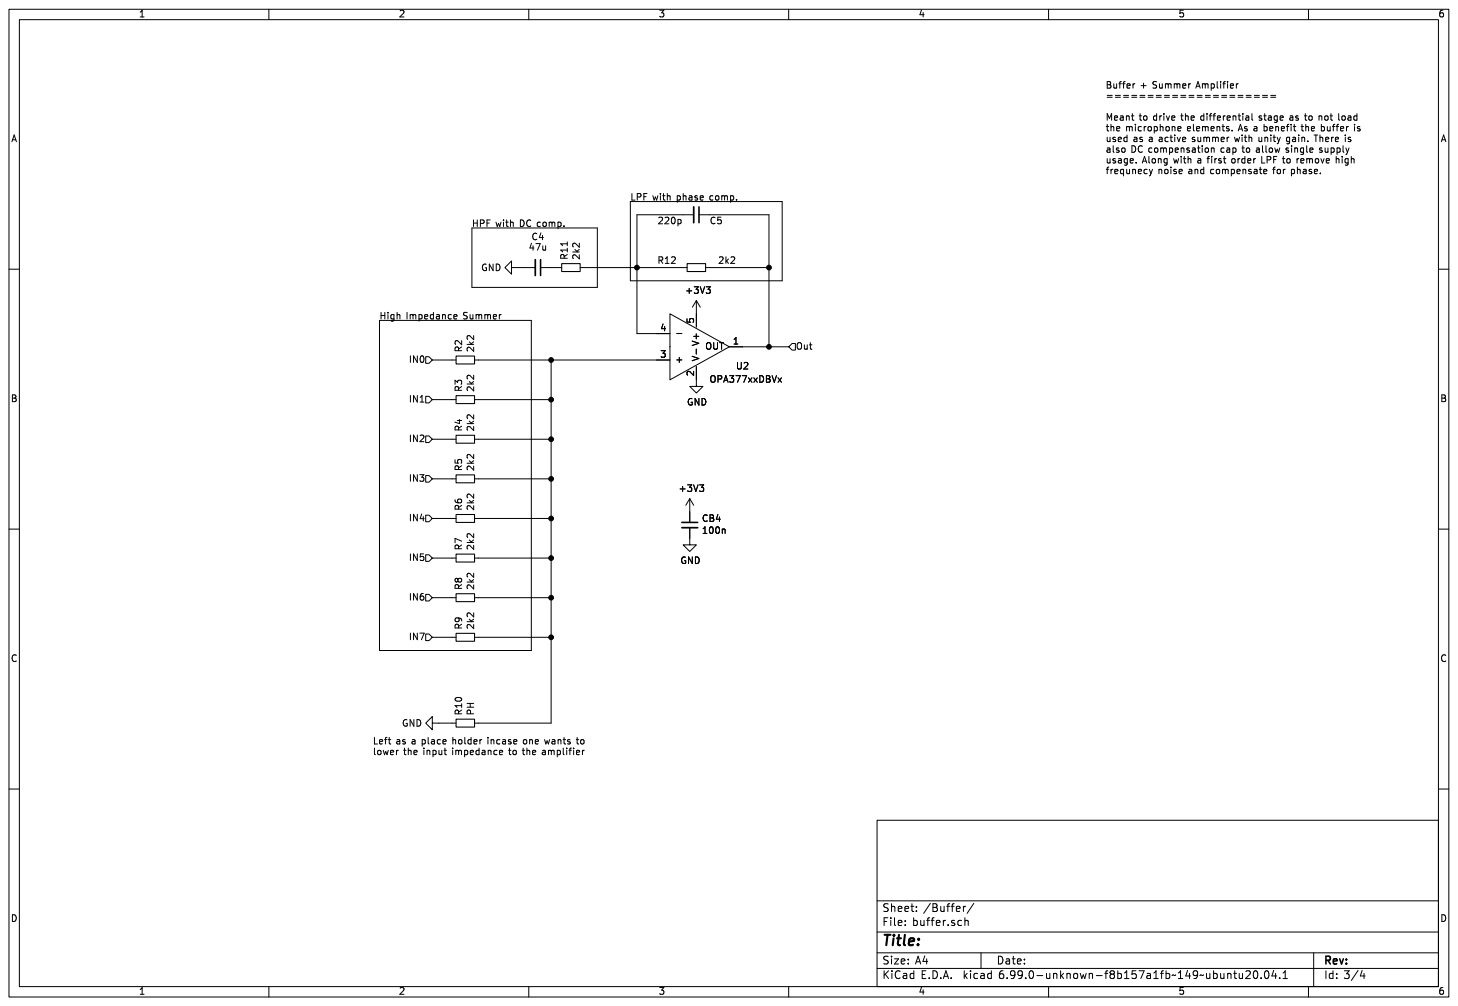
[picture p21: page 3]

Buffer + Summer Amplifier ===================== Meant to drive the differential stage as to not load

the microphone elements. As a benefit the buffer is
used as a active summer with unity gain. There is
also DC compensation cap to allow single supply
usage. Along with a first order LPF to remove high
frequnecy noise and compensate for phase.

LPF with phase comp.

HPF with DC comp.

Left as a place holder incase one wants to

Id: 3/4 Title: File: buffer.sch Sheet: /Buffer/

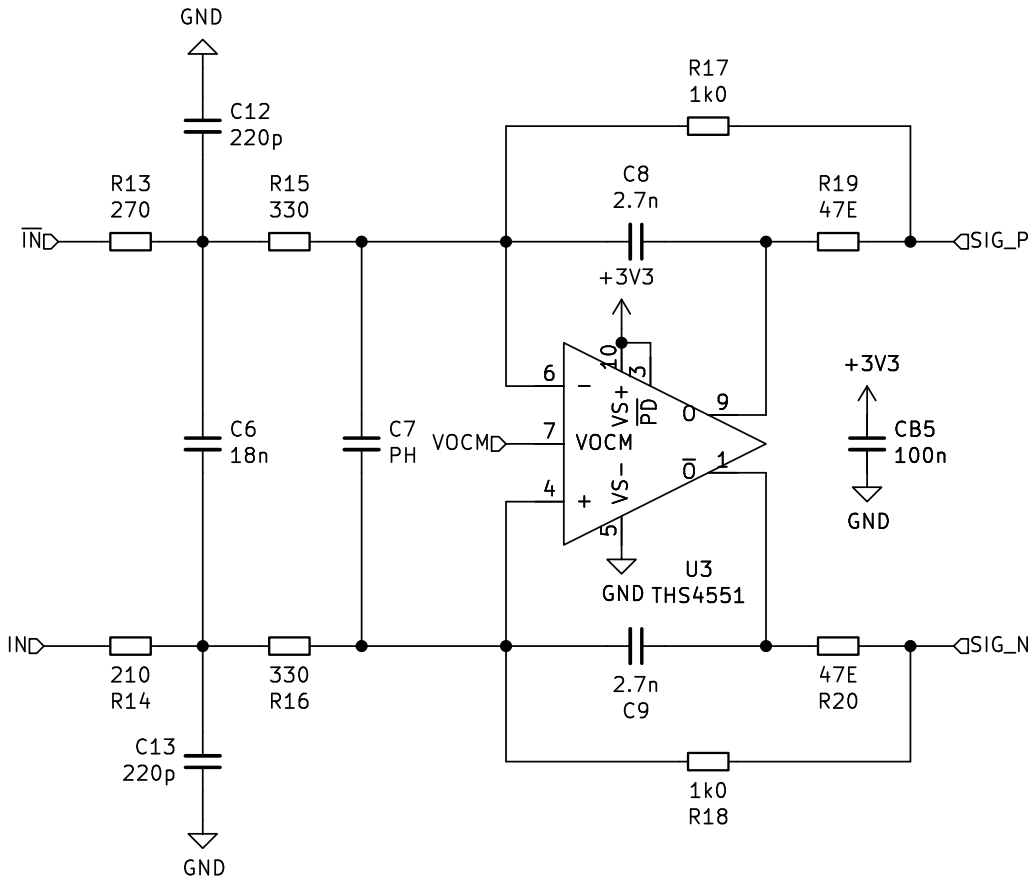
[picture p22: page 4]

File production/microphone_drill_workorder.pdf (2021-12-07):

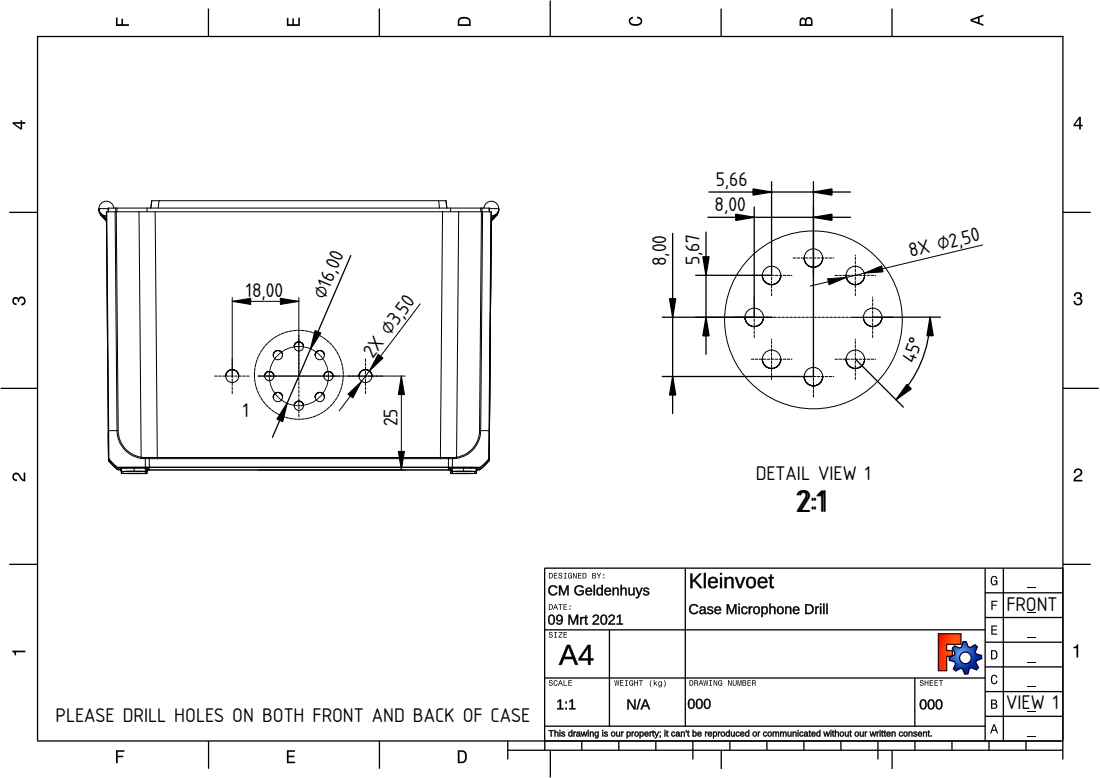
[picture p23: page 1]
DETAIL VIEW 1; FRONT

VIEW 1 PLEASE DRILL HOLES ON BOTH FRONT AND BACK OF CASE

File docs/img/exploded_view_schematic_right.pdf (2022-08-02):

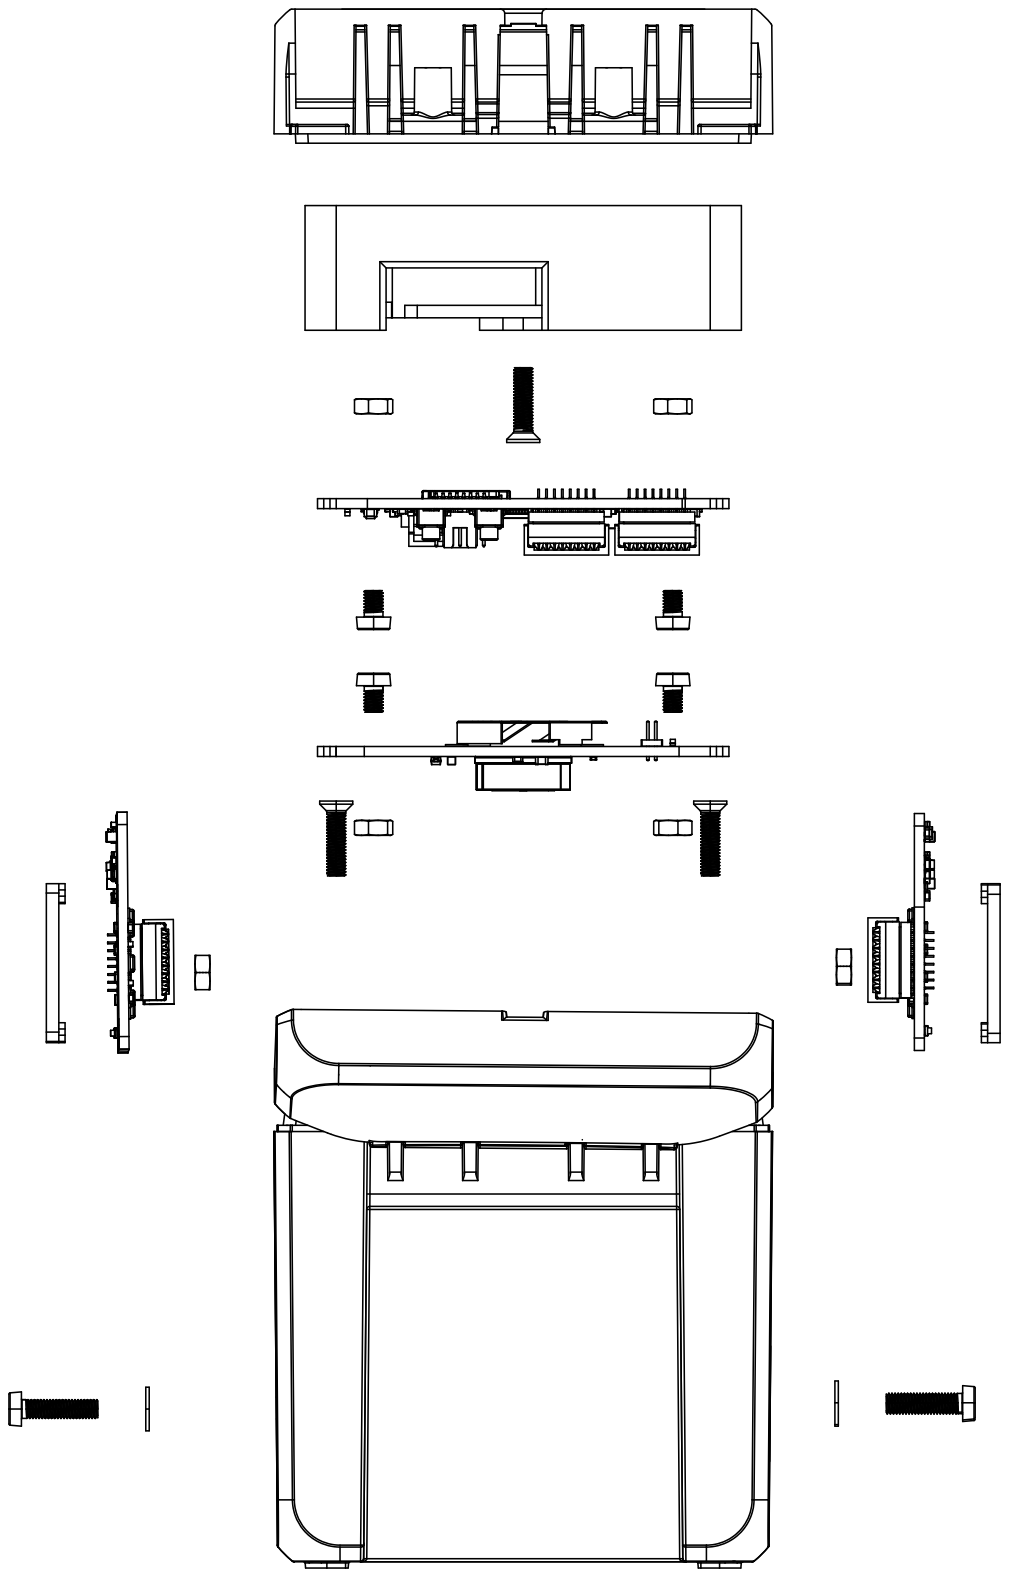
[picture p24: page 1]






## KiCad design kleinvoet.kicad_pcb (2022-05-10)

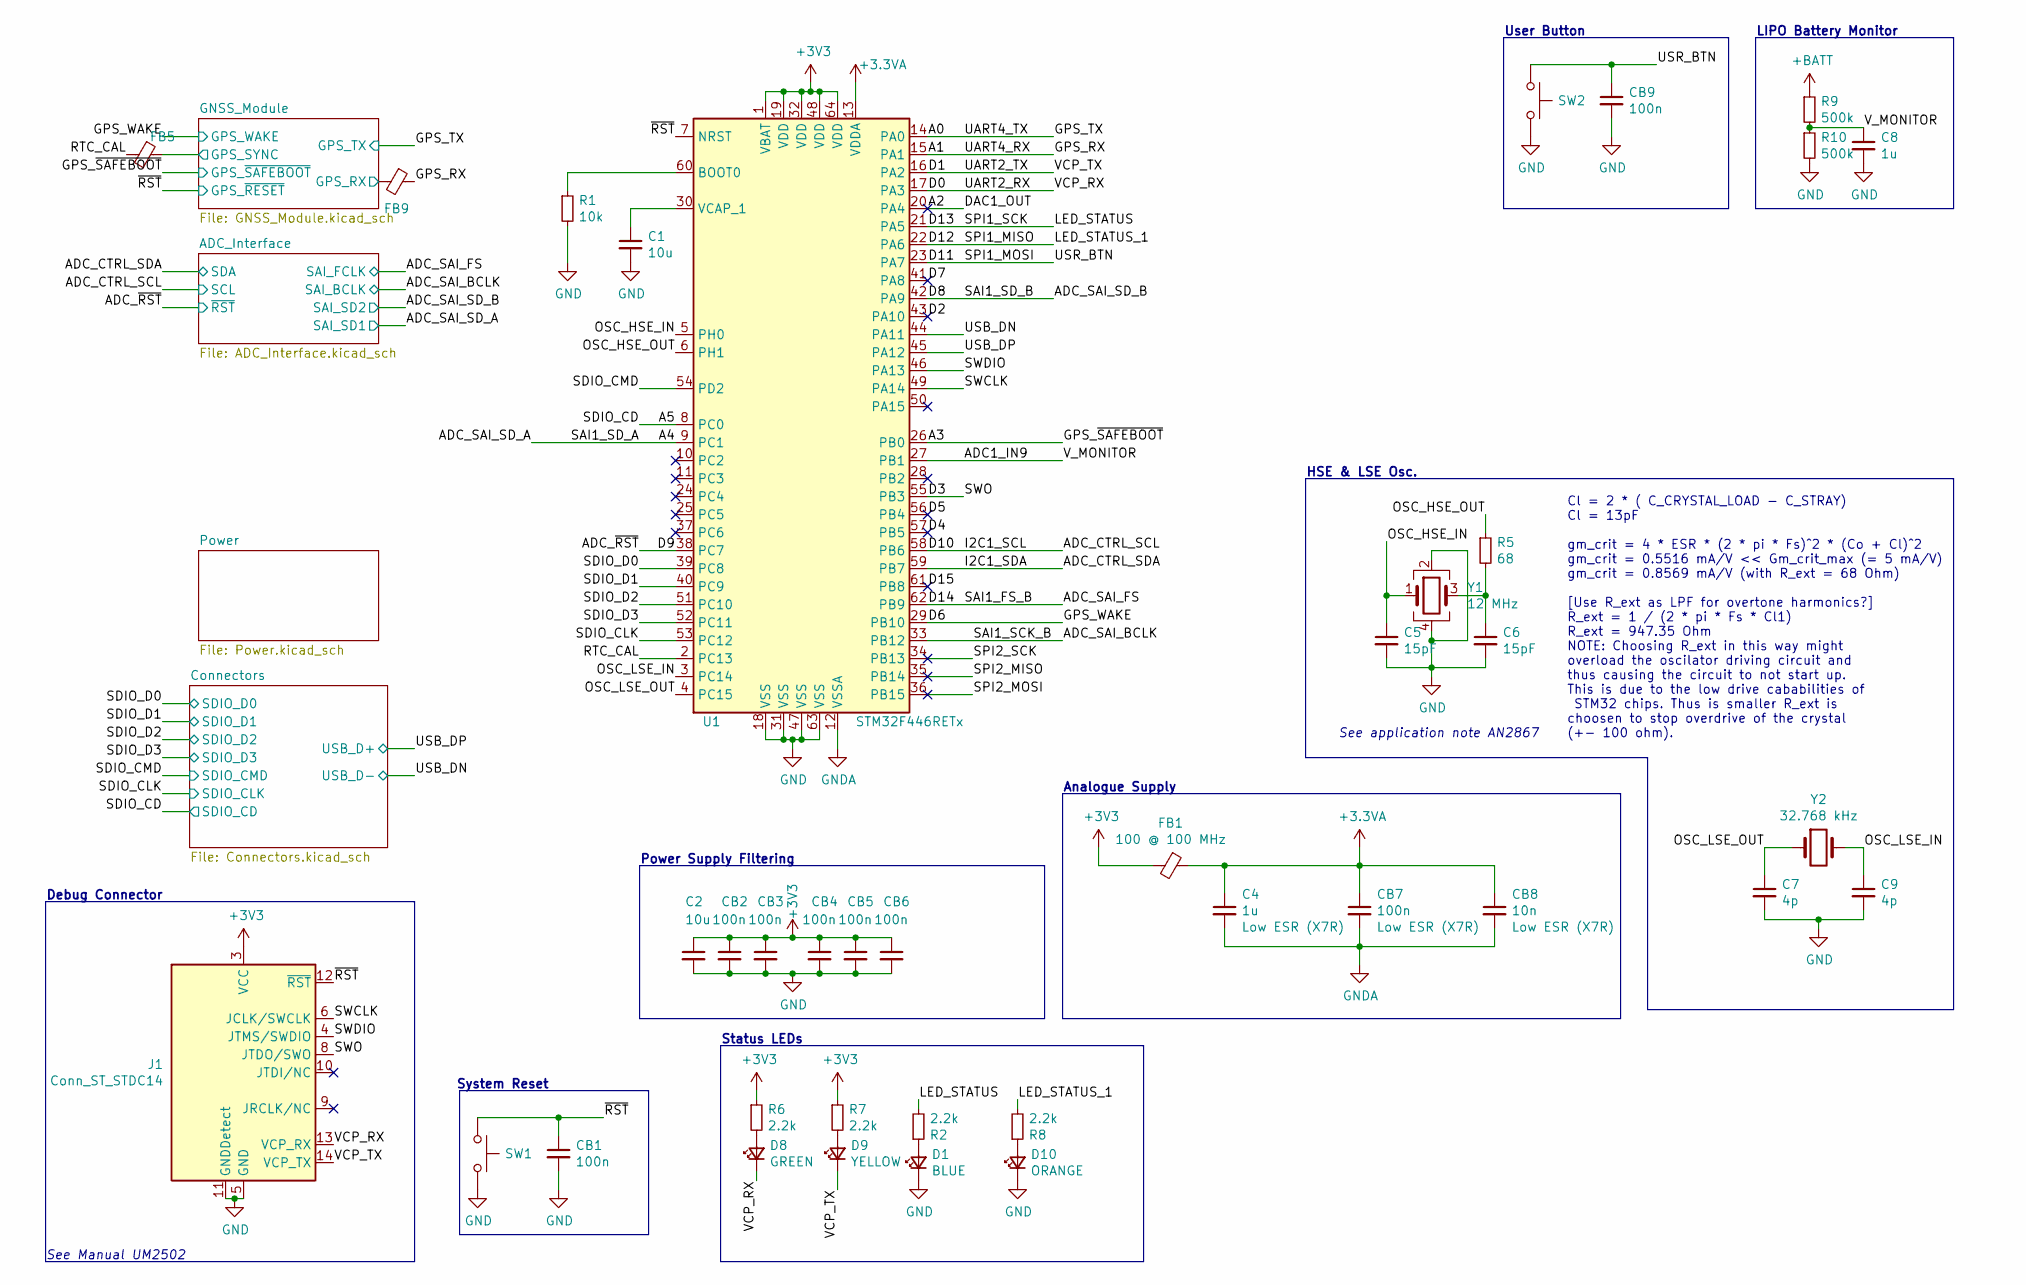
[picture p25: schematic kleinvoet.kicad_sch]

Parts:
C1, C2: 10u; C_0805_2012Metric_Pad1.18x1.45mm_HandSolder; MPN C0805C106K9PACTU
C4, C8: 1u; C_0603_1608Metric_Pad1.08x0.95mm_HandSolder; MPN C0603C105K8RACTU
C5, C6: 15pF; C_0603_1608Metric_Pad1.08x0.95mm_HandSolder; MPN C0603C150J5GACTU
C7, C9: 4p; C_0603_1608Metric_Pad1.08x0.95mm_HandSolder; MPN C1608C0G1H040C080AA
CB1, CB2, CB3, CB4, CB5, CB6, CB7, CB9: 100n; C_0603_1608Metric_Pad1.08x0.95mm_HandSolder; MPN C0603C104M5RACTU
CB8: 10n; C_0603_1608Metric_Pad1.08x0.95mm_HandSolder; MPN C0603C103J5RACTU
D1: BLUE; LED_0603_1608Metric_Pad1.05x0.95mm_HandSolder; MPN SMLD12BN1WT86
D8: GREEN; LED_0603_1608Metric_Pad1.05x0.95mm_HandSolder; MPN SMLD12EN1WT86
D9: YELLOW; LED_0603_1608Metric_Pad1.05x0.95mm_HandSolder; MPN SML-D12Y8WT86C
D10: ORANGE; LED_0603_1608Metric_Pad1.05x0.95mm_HandSolder; MPN SML-D12D8WT86C
FB1: BLM18KG101TZ1D; L_0603_1608Metric_Pad1.05x0.95mm_HandSolder; MPN BLM18KG101TZ1D
FB5, FB9: BLM15HD102SN1; L_0603_1608Metric_Pad1.05x0.95mm_HandSolder; MPN BLM15HD102SN1D
J1: Conn_ST_STDC14; SAMTEC-FTSH-107-01-X-DV; MPN FTSH-107-01-F-DV-K
R1: 10k; R_0603_1608Metric_Pad0.98x0.95mm_HandSolder; MPN RC0603JR-0710KL
R2, R6, R7, R8: 2.2k; R_0603_1608Metric_Pad0.98x0.95mm_HandSolder; MPN RC0603FR-072K2L
R5: 68; R_0603_1608Metric_Pad0.98x0.95mm_HandSolder; MPN RC0603FR-1068RL
R9, R10: 500k; R_0603_1608Metric_Pad0.98x0.95mm_HandSolder; MPN RC0603FR-07470KL
SW1: RESET; SW_SPST_PTS647; MPN PTS647SN50SMTR2LFS
SW2: USER; SW_SPST_PTS647; MPN PTS647SN50SMTR2LFS
U1: STM32F446RETx; LQFP-64_10x10mm_P0.5mm; MPN STM32F446RCT6
Y1: 12 MHz; ECS-33B; MPN ECS-120-12-33-AEN-TR
Y2: 32.768 kHz; ECX-31B; MPN ECS-.327-7-34B-TR

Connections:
+3.3VA: C4.1, CB7.1, CB8.1, FB1.1, U1.13 (VDDA)
+3V3: C2.1, CB2.1, CB3.1, CB4.1, CB5.1, CB6.1, FB1.2, J1.3 (VCC), R6.1, R7.1, U1.1 (VBAT), U1.19 (VDD), U1.32 (VDD), U1.48 (VDD), U1.64 (VDD); also elsewhere on the board
+BATT: R9.1; also elsewhere on the board
/A0: U1.14 (PA0); also elsewhere on the board
/A1: FB9.1, U1.15 (PA1)
/A2: U1.20 (PA4)
/A3: U1.26 (PB0); also elsewhere on the board
/A4: U1.9 (PC1); also elsewhere on the board
/A5: U1.8 (PC0); also elsewhere on the board
/ADC1_IN9: C8.1, R9.2, R10.1, U1.27 (PB1)
/ADC_CTRL_SCL: U1.58 (PB6); also elsewhere on the board
/ADC_CTRL_SDA: U1.59 (PB7); also elsewhere on the board
/ADC_SAI_BCLK: U1.33 (PB12); also elsewhere on the board
/ADC_SAI_FS: U1.62 (PB9); also elsewhere on the board
/ADC_SAI_SD_B: U1.42 (PA9); also elsewhere on the board
/ADC_~RST: U1.38 (PC7); also elsewhere on the board
/D0: D8.1 (K), J1.13 (VCP_RX), U1.17 (PA3)
/D1: D9.1 (K), J1.14 (VCP_TX), U1.16 (PA2)
/D2: U1.43 (PA10)
/D3: J1.8 (JTDO/SWO), U1.55 (PB3)
/D4: U1.57 (PB5)
/D5: U1.56 (PB4)
/D6: U1.29 (PB10); also elsewhere on the board
/D7: U1.41 (PA8)
/D11: CB9.1, SW2.1, U1.23 (PA7)
/D12: R8.2, U1.22 (PA6)
/D13: R2.2, U1.21 (PA5)
/D15: U1.61 (PB8)
/GNSS_Module/GPS_RX: FB9.2; also elsewhere on the board
/GNSS_Module/GPS_SYNC: FB5.1; also elsewhere on the board
/OSC_HSE_IN: C5.1, U1.5 (PH0), Y1.1
/OSC_HSE_OUT: R5.1, U1.6 (PH1)
/OSC_LSE_IN: C9.1, U1.3 (PC14), Y2.2
/OSC_LSE_OUT: C7.1, U1.4 (PC15), Y2.1
/RTC_CAL: FB5.2, U1.2 (PC13)
/SDIO_CLK: U1.53 (PC12); also elsewhere on the board
/SDIO_CMD: U1.54 (PD2); also elsewhere on the board
/SDIO_D0: U1.39 (PC8); also elsewhere on the board
/SDIO_D1: U1.40 (PC9); also elsewhere on the board
/SDIO_D2: U1.51 (PC10); also elsewhere on the board
/SDIO_D3: U1.52 (PC11); also elsewhere on the board
/SPI2_MISO: U1.35 (PB14)
/SPI2_MOSI: U1.36 (PB15)
/SPI2_SCK: U1.34 (PB13)
/SWCLK: J1.6 (JCLK/SWCLK), U1.49 (PA14)
/SWDIO: J1.4 (JTMS/SWDIO), U1.46 (PA13)
/USB_DN: U1.44 (PA11); also elsewhere on the board
/USB_DP: U1.45 (PA12); also elsewhere on the board
/~RST: CB1.1, J1.12 (~RST), SW1.1, U1.7 (NRST); also elsewhere on the board
GND: C1.2, C2.2, C4.2, C5.2, C6.2, C7.2, C8.2, C9.2, CB1.2, CB2.2, CB3.2, CB4.2, CB5.2, CB6.2, CB7.2, CB8.2, CB9.2, D1.1 (K), D10.1 (K), J1.5 (GND), J1.7 (GND), J1.11 (GNDDetect), R1.2, R10.2, SW1.2, SW2.2, U1.12 (VSSA), U1.18 (VSS), U1.31 (VSS), U1.47 (VSS), U1.63 (VSS), Y1.2, Y1.4; also elsewhere on the board
unnamed: C1.1, U1.30 (VCAP_1)
unnamed: C6.1, R5.2, Y1.3
unnamed: D1.2 (A), R2.1
unnamed: D8.2 (A), R6.2
unnamed: D9.2 (A), R7.2
unnamed: D10.2 (A), R8.1
unnamed: R1.1, U1.60 (BOOT0)

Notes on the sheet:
Cl = 2 * ( C_CRYSTAL_LOAD - C_STRAY) Cl = 13pF gm_crit = 4 * ESR * (2 * pi * Fs)^2 * (Co + Cl)^2 gm_crit = 0.5516 mA/V << Gm_crit_max (= 5 mA/V) gm_crit = 0.8569 mA/V (with R_ext = 68 Ohm) [Use R_ext as LPF for overtone harmonics?] R_ext = 1 / (2 * pi * Fs * Cl1) R_ext = 947.35 Ohm NOTE: Choosing R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
User Button
System Reset
Status LEDs
LIPO Battery Monitor
HSE & LSE Osc.
Power Supply Filtering
Debug Connector
See Manual UM2502
See application note AN2867
Analogue Supply

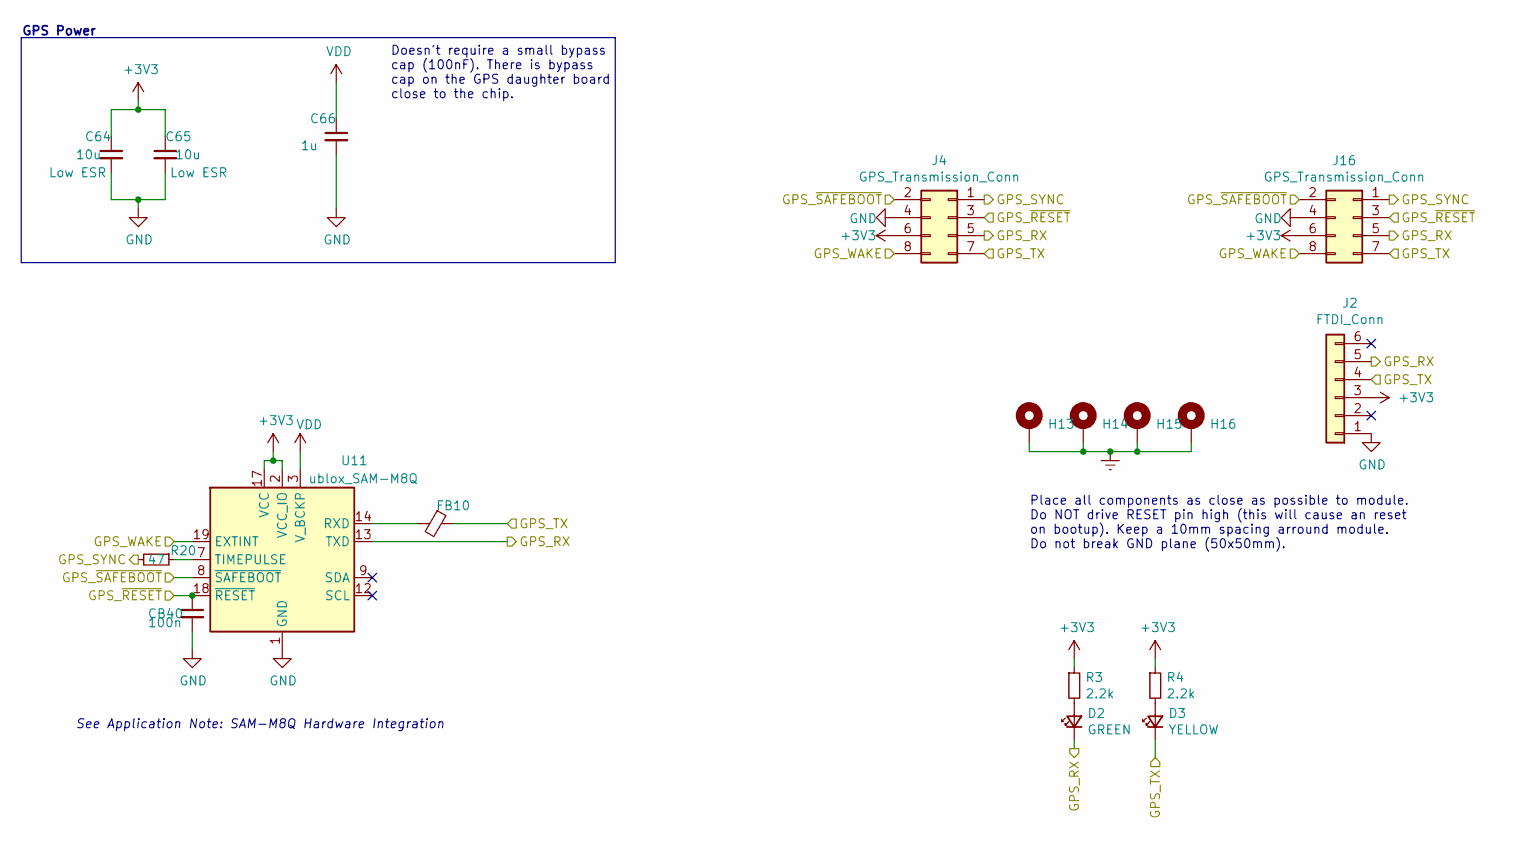
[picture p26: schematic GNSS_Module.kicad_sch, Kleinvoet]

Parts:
C64, C65: 10u; C_0805_2012Metric_Pad1.18x1.45mm_HandSolder; MPN C0805C106K9PACTU
C66: 1u; C_0603_1608Metric_Pad1.08x0.95mm_HandSolder; MPN C0603C105K8RACTU
CB40: 100n; C_0603_1608Metric_Pad1.08x0.95mm_HandSolder; MPN C0603C104M5RACTU
D2: GREEN; LED_0603_1608Metric_Pad1.05x0.95mm_HandSolder; MPN SMLD12EN1WT86
D3: YELLOW; LED_0603_1608Metric_Pad1.05x0.95mm_HandSolder; MPN SML-D12Y8WT86C
FB10: BLM15HD102SN1; L_0402_1005Metric; MPN BLM15HD102SN1D
H13, H14, H15, H16: MountingHole_Pad; MountingHole_3.2mm_M3_Pad_Via
J2: FTDI_Conn; PinHeader_1x06_P2.54mm_Vertical
J4, J16: GPS_Transmission_Conn; PinHeader_2x04_P1.27mm_Vertical; MPN FTSH-104-01-F-D
R3, R4: 2.2k; R_0603_1608Metric_Pad0.98x0.95mm_HandSolder; MPN RC0603FR-072K2L
R20: 47; R_0603_1608Metric_Pad0.98x0.95mm_HandSolder; MPN ERJ-3EKF47R0V
U11: ublox_SAM-M8Q; ublox_SAM-M8Q_HandSolder; MPN SAM-M8Q

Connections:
+3V3: C64.1, C65.1, J2.3, J4.6, J16.6, R3.1, R4.1, U11.2 (VCC_IO), U11.17 (VCC); also elsewhere on the board
/A0: D3.1 (K), FB10.1, J2.4, J4.7, J16.7; also elsewhere on the board
/A3: J4.2, J16.2, U11.8 (~SAFEBOOT); also elsewhere on the board
/D6: J4.8, J16.8, U11.19 (EXTINT); also elsewhere on the board
/GNSS_Module/GPS_RX: D2.1 (K), J2.5, J4.5, J16.5, U11.13 (TXD); also elsewhere on the board
/GNSS_Module/GPS_SYNC: J4.1, J16.1, R20.2; also elsewhere on the board
/~RST: CB40.1, J4.3, J16.3, U11.18 (~RESET); also elsewhere on the board
Earth: H13.1, H14.1, H15.1, H16.1; also elsewhere on the board
GND: C64.2, C65.2, C66.2, CB40.2, J2.1, J4.4, J16.4, U11.1 (GND), U11.4 (GND), U11.5 (GND), U11.6 (GND), U11.10 (GND), U11.11 (GND), U11.15 (GND), U11.16 (GND), U11.20 (GND); also elsewhere on the board
unnamed: D2.2 (A), R3.2
unnamed: D3.2 (A), R4.2
unnamed: FB10.2, U11.14 (RXD)
unnamed: R20.1, U11.7 (TIMEPULSE)
VDD: C66.1, U11.3 (V_BCKP); also elsewhere on the board

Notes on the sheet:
See Application Note: SAM-M8Q Hardware Integration
Place all components as close as possible to module. Do NOT drive RESET pin high (this will cause an reset on bootup). Keep a 10mm spacing arround module. Do not break GND plane (50x50mm).
GPS Power
Doesn't require a small bypass cap (100nF). There is bypass cap on the GPS daughter board close to the chip.

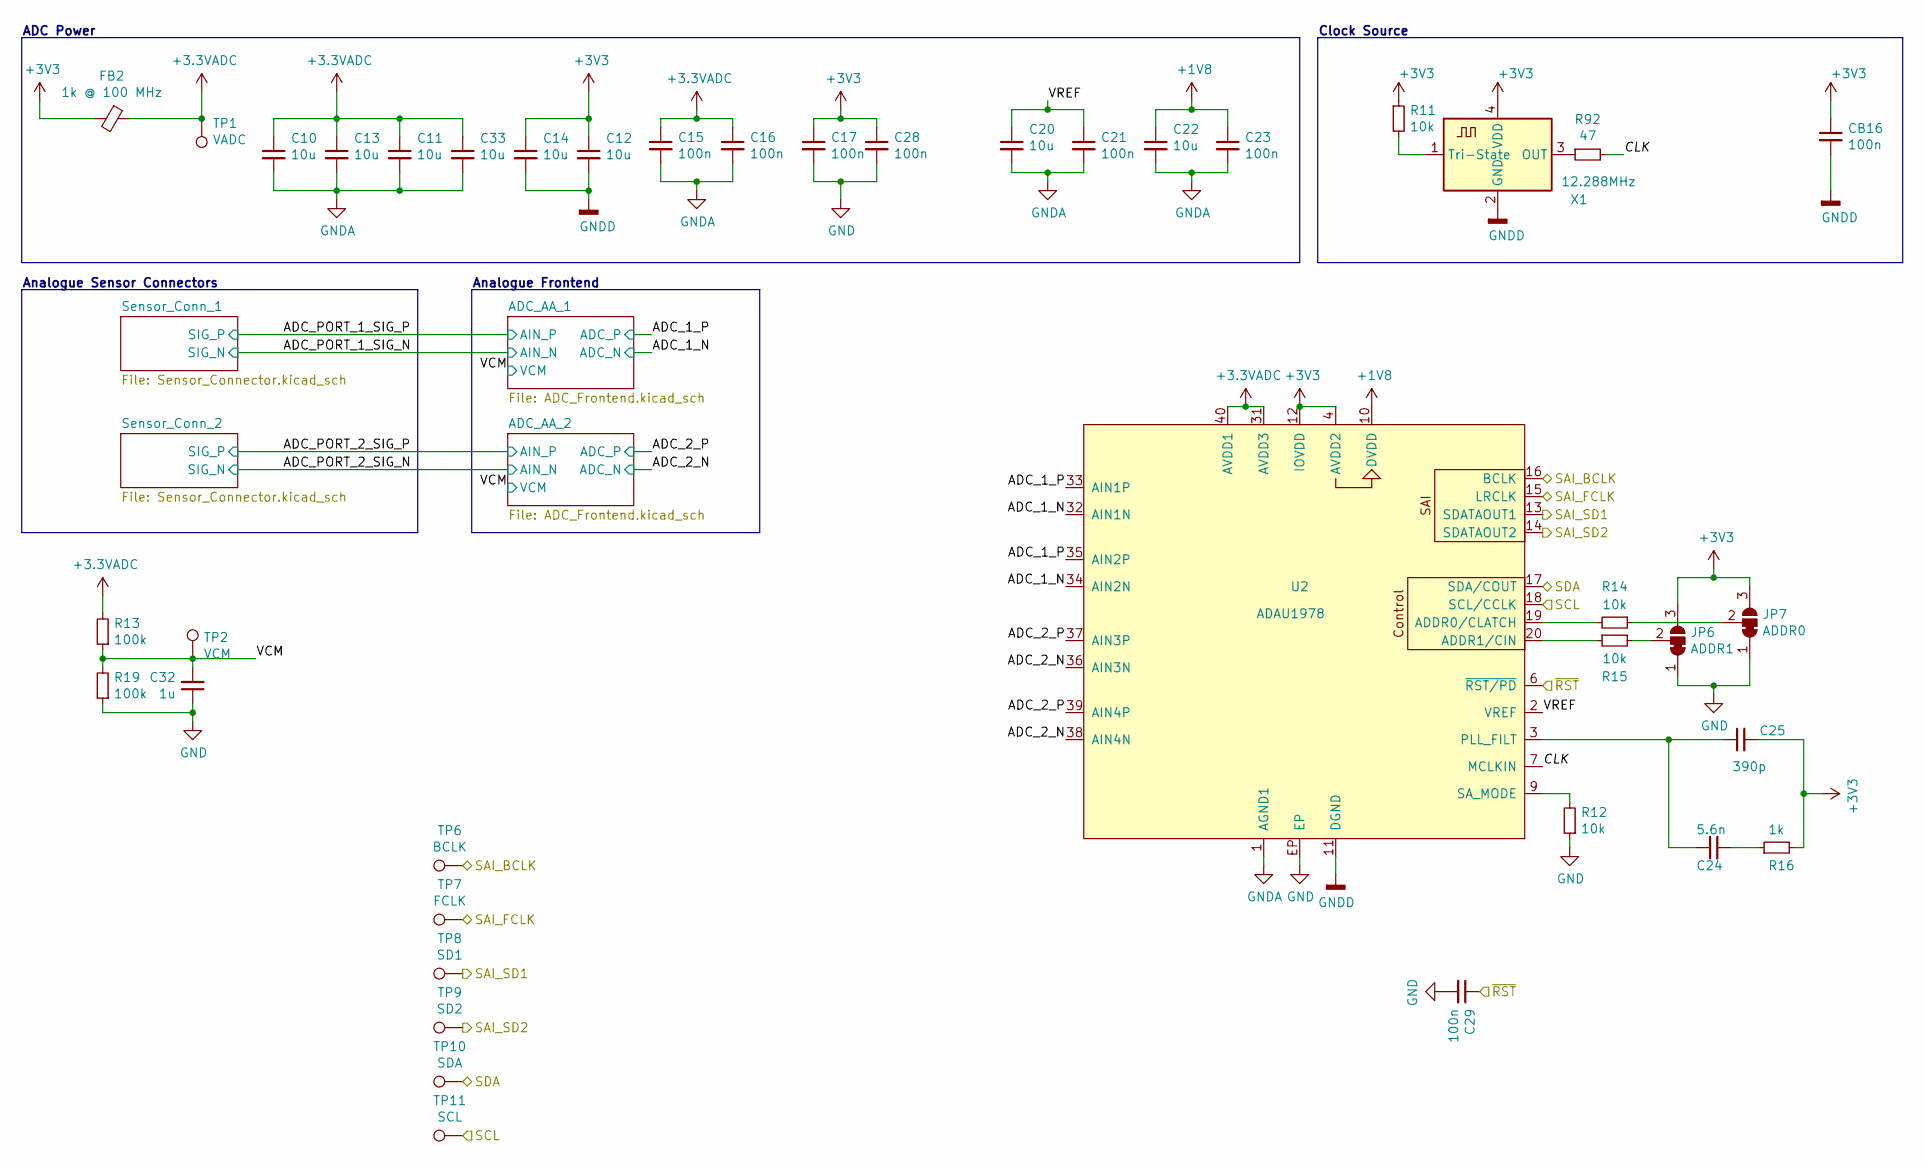
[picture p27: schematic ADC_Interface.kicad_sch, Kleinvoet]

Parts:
C10, C11, C12, C13, C14, C20, C22, C33: 10u; C_0805_2012Metric_Pad1.18x1.45mm_HandSolder; MPN C0805C106K9PACTU
C15, C16, C17, C21, C23, C28, C29: 100n; C_0603_1608Metric_Pad1.08x0.95mm_HandSolder; MPN C0603C104M5RACTU
C24: 5.6n; C_0603_1608Metric_Pad1.08x0.95mm_HandSolder; MPN CC0603JRX7R9BB562
C25: 390p; C_0603_1608Metric_Pad1.08x0.95mm_HandSolder; MPN CC0603JRNPO9BN391
C32: 1u; C_0603_1608Metric_Pad1.08x0.95mm_HandSolder; MPN C0603C105K8RACTU
CB16: 100n; C_0603_1608Metric_Pad1.08x0.95mm_HandSolder; MPN C0603C104M5RACTU
FB2: BLM18KG101TZ1D; L_0603_1608Metric_Pad1.05x0.95mm_HandSolder; MPN BLM18KG101TZ1D
JP6: ADDR1; SolderJumper-3_P1.3mm_Bridged12_RoundedPad1.0x1.5mm_NumberL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
JP7: ADDR0; SolderJumper-3_P1.3mm_Bridged12_RoundedPad1.0x1.5mm_NumberL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
R11, R12, R14, R15: 10k; R_0603_1608Metric_Pad0.98x0.95mm_HandSolder; MPN RC0603JR-0710KL
R13, R19: 100k; R_0603_1608Metric_Pad0.98x0.95mm_HandSolder; MPN RC0603FR-07100KL
R16: 1k; R_0603_1608Metric_Pad0.98x0.95mm_HandSolder; MPN RC0603FR-071KL
R92: 47; R_0603_1608Metric_Pad0.98x0.95mm_HandSolder; MPN ERJ-3EKF47R0V
TP1: VADC; TestPoint_Pad_D1.0mm
TP2: VCM; TestPoint_Pad_D1.0mm
TP6: BCLK; TestPoint_Pad_D1.0mm
TP7: FCLK; TestPoint_Pad_D1.0mm
TP8: SD1; TestPoint_Pad_D1.0mm
TP9: SD2; TestPoint_Pad_D1.0mm
TP10: SDA; TestPoint_Pad_D1.0mm
TP11: SCL; TestPoint_Pad_D1.0mm
U2: ADAU1978; LFCSP-WQ-40-1EP_6x6mm_P0.5_CP-40-14; MPN ADAU1978WBCPZ-RL
X1: 12.288MHz; ECS-TXO-3225MV; MPN ECS-TXO-3225MV-122.8-TR

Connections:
+1V8: C22.1, C23.1, U2.10 (DVDD)
+3.3VADC: C10.1, C11.1, C13.1, C15.1, C16.1, C33.1, FB2.1, R13.2, TP1.1, U2.31 (AVDD3), U2.40 (AVDD1); also elsewhere on the board
+3V3: C12.1, C14.1, C17.1, C25.2, C28.1, CB16.1, FB2.2, JP6.3 (B), JP7.3 (B), R11.1, R16.2, U2.4 (AVDD2), U2.12 (IOVDD), X1.4 (VDD); also elsewhere on the board
/A4: TP8.1, U2.13 (SDATAOUT1); also elsewhere on the board
/ADC_CTRL_SCL: TP11.1, U2.18 (SCL/CCLK); also elsewhere on the board
/ADC_CTRL_SDA: TP10.1, U2.17 (SDA/COUT); also elsewhere on the board
/ADC_Interface/ADC_1_N: U2.32 (AIN1N), U2.34 (AIN2N); also elsewhere on the board
/ADC_Interface/ADC_1_P: U2.33 (AIN1P), U2.35 (AIN2P); also elsewhere on the board
/ADC_Interface/ADC_2_N: U2.36 (AIN3N), U2.38 (AIN4N); also elsewhere on the board
/ADC_Interface/ADC_2_P: U2.37 (AIN3P), U2.39 (AIN4P); also elsewhere on the board
/ADC_Interface/CLK: R92.2, U2.7 (MCLKIN)
/ADC_Interface/VCM: C32.2, R13.1, R19.2, TP2.1; also elsewhere on the board
/ADC_Interface/VREF: C20.1, C21.1, U2.2 (VREF)
/ADC_SAI_BCLK: TP6.1, U2.16 (BCLK); also elsewhere on the board
/ADC_SAI_FS: TP7.1, U2.15 (LRCLK); also elsewhere on the board
/ADC_SAI_SD_B: TP9.1, U2.14 (SDATAOUT2); also elsewhere on the board
/ADC_~RST: C29.1, U2.6 (~RST/PD); also elsewhere on the board
GND: C10.2, C11.2, C12.2, C13.2, C14.2, C15.2, C16.2, C17.2, C20.2, C21.2, C22.2, C23.2, C28.2, C29.2, C32.1, C33.2, CB16.2, JP6.1 (A), JP7.1 (A), R12.1, R19.1, U2.1 (AGND1), U2.5 (AGND2), U2.11 (DGND), U2.21 (AGND3), U2.22 (AGND4), U2.28 (AGND5), U2.29 (AGND6), U2.EP, X1.2 (GND); also elsewhere on the board
unnamed: C24.1, C25.1, U2.3 (PLL_FILT)
unnamed: C24.2, R16.1
unnamed: JP6.2 (C), R15.2
unnamed: JP7.2 (C), R14.1
unnamed: R11.2, X1.1 (Tri-State)
unnamed: R12.2, U2.9 (SA_MODE)
unnamed: R14.2, U2.19 (ADDR0/CLATCH)
unnamed: R15.1, U2.20 (ADDR1/CIN)
unnamed: R92.1, X1.3 (OUT)

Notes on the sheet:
ADC Power
Clock Source
Analogue Frontend
Analogue Sensor Connectors

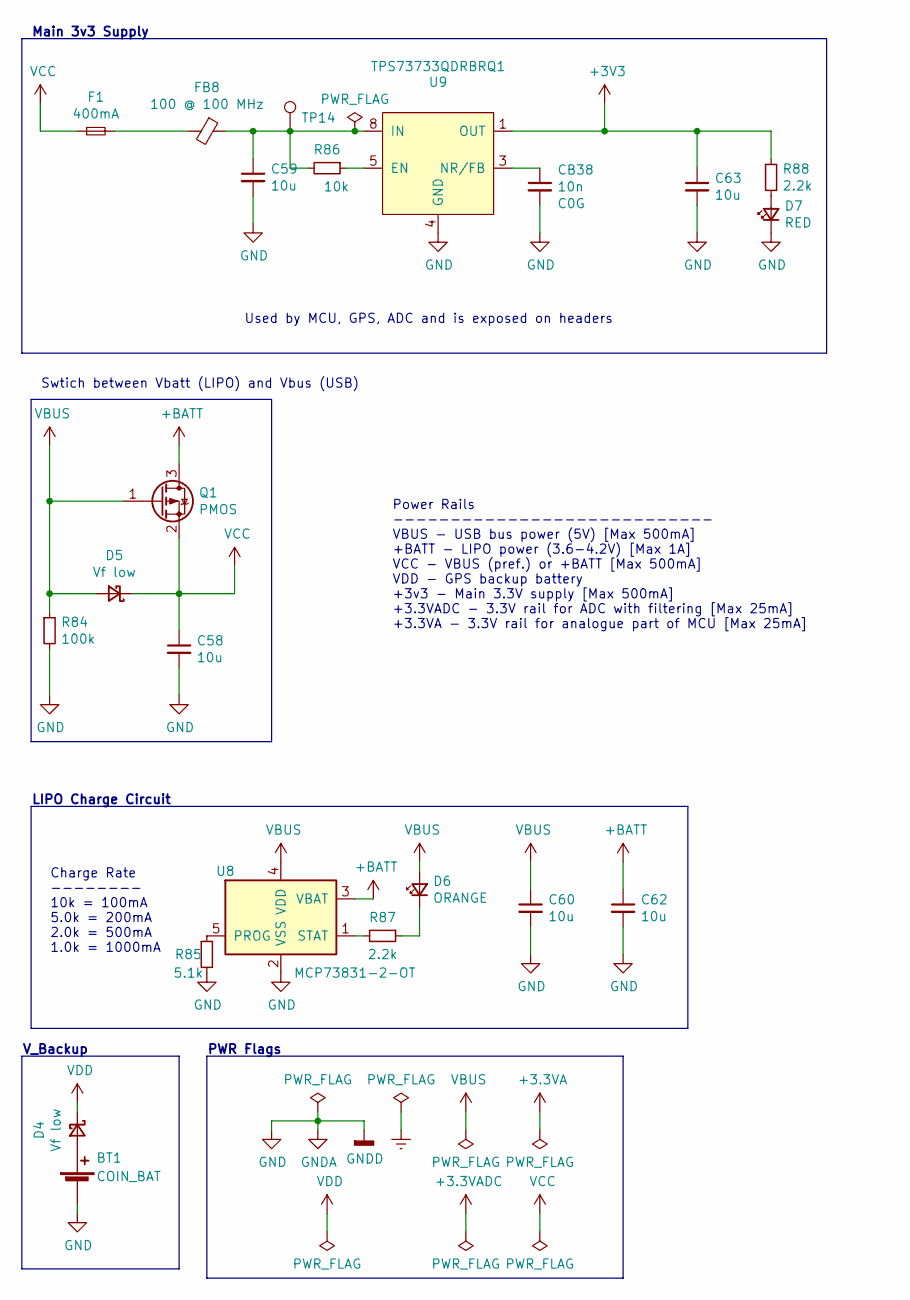
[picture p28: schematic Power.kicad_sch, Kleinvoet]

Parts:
BT1: COIN_BAT; BatteryHolder_Keystone_3002_1x2032; MPN 2898
C58, C59, C60, C62, C63: 10u; C_0805_2012Metric_Pad1.18x1.45mm_HandSolder; MPN C0805C106K9PACTU
CB38: 10n; C_0603_1608Metric_Pad1.08x0.95mm_HandSolder; MPN C0603C103J5RACTU
D4, D5: Vf low; D_SOD-123; MPN RSX101MM-30TR
D6: ORANGE; LED_0603_1608Metric_Pad1.05x0.95mm_HandSolder; MPN SML-D12D8WT86C
D7: RED; LED_0603_1608Metric_Pad1.05x0.95mm_HandSolder; MPN SML-D12U8WT86C
F1: 400mA; Fuse_0603_1608Metric_Pad1.05x0.95mm_HandSolder; MPN 0ZCM0020FF2G
FB8: 100 @ 100 MHz; L_0603_1608Metric_Pad1.05x0.95mm_HandSolder; MPN BLM18EG101TZ1D
Q1: PMOS; SOT-23_Handsoldering; MPN NTR3A30PZT1G
R84: 100k; R_0603_1608Metric_Pad0.98x0.95mm_HandSolder; MPN RC0603FR-07100KL
R85: 5.1k; R_0603_1608Metric_Pad0.98x0.95mm_HandSolder; MPN AC0603FR-135K1L
R86: 10k; R_0603_1608Metric_Pad0.98x0.95mm_HandSolder; MPN RC0603JR-0710KL
R87, R88: 2.2k; R_0603_1608Metric_Pad0.98x0.95mm_HandSolder; MPN RC0603FR-072K2L
TP14: VIN; TestPoint_Pad_D1.0mm
U8: MCP73831-2-OT; SOT-23-5; MPN MCP73831T-2ACI/OT
U9: TPS73733QDRBRQ1; Texas_DRB0008A; MPN TPS73733QDRBRQ1

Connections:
+3V3: C63.1, R88.1, U9.1 (OUT); also elsewhere on the board
+BATT: C62.1, Q1.3 (D), U8.3 (VBAT); also elsewhere on the board
GND: BT1.2 (-), C58.2, C59.2, C60.2, C62.2, C63.2, CB38.2, D7.1 (K), R84.2, R85.2, U8.2 (VSS), U9.4 (GND), U9.9 (GND); also elsewhere on the board
unnamed: BT1.1 (+), D4.2 (A)
unnamed: C59.1, FB8.1, R86.2, TP14.1, U9.8 (IN)
unnamed: CB38.1, U9.3 (NR/FB)
unnamed: D6.1 (K), R87.1
unnamed: D7.2 (A), R88.2
unnamed: F1.2, FB8.2
unnamed: R85.1, U8.5 (PROG)
unnamed: R86.1, U9.5 (EN)
unnamed: R87.2, U8.1 (STAT)
VBUS: C60.1, D5.2 (A), D6.2 (A), Q1.1 (G), R84.1, U8.4 (VDD); also elsewhere on the board
VCC: C58.1, D5.1 (K), F1.1, Q1.2 (S)
VDD: D4.1 (K); also elsewhere on the board

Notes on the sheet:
LIPO Charge Circuit
Swtich between Vbatt (LIPO) and Vbus (USB)
Charge Rate -------- 10k = 100mA 5.0k = 200mA 2.0k = 500mA 1.0k = 1000mA
Main 3v3 Supply
PWR Flags
V_Backup
Power Rails ---------------------------- VBUS - USB bus power (5V) [Max 500mA] +BATT - LIPO power (3.6-4.2V) [Max 1A] VCC - VBUS (pref.) or +BATT [Max 500mA] VDD - GPS backup battery +3v3 - Main 3.3V supply [Max 500mA] +3.3VADC - 3.3V rail for ADC with filtering [Max 25mA] +3.3VA - 3.3V rail for an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
Used by MCU, GPS, ADC and is exposed on headers

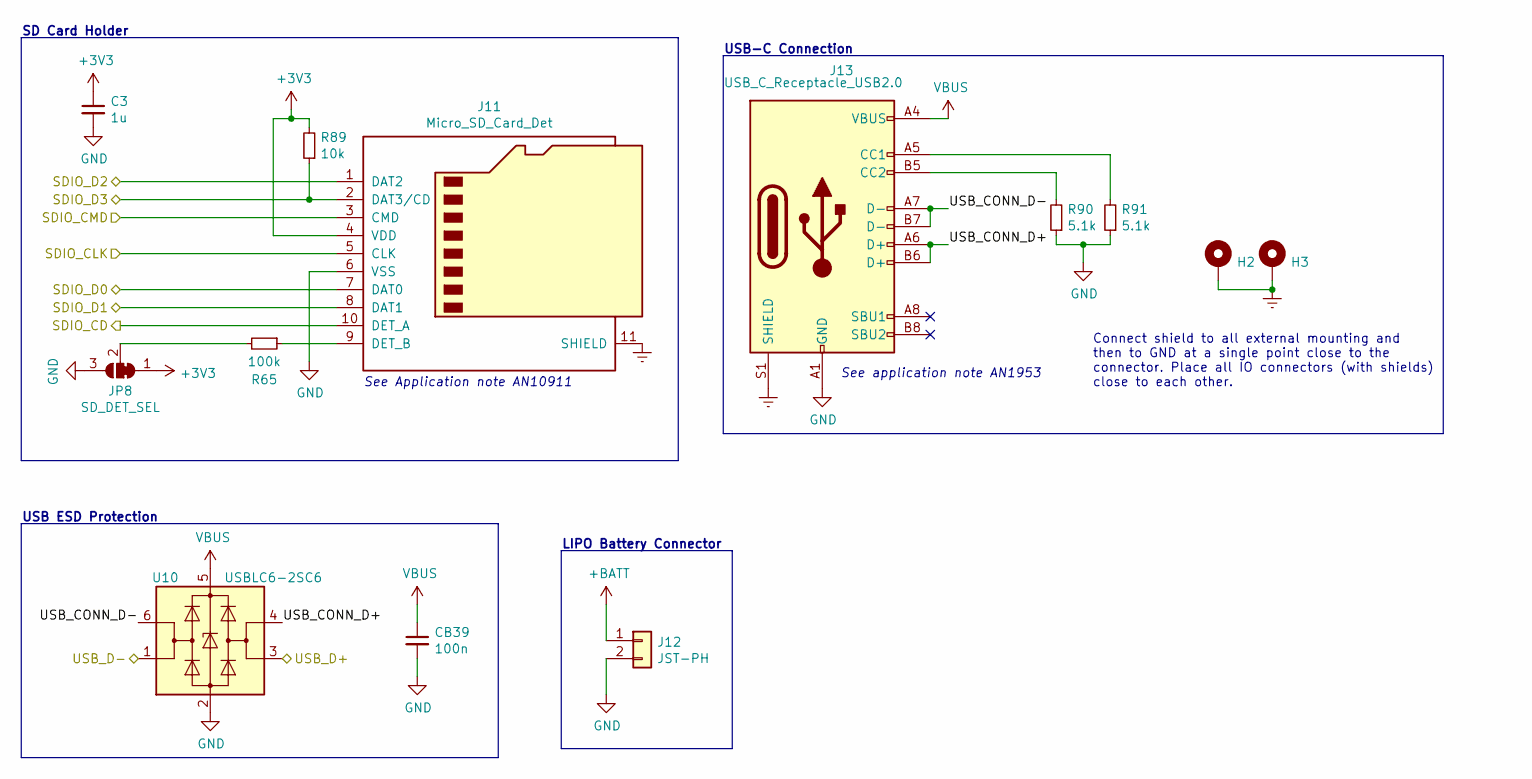
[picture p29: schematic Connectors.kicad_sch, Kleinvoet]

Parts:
C3: 1u; C_0603_1608Metric_Pad1.08x0.95mm_HandSolder; MPN C0603C105K8RACTU
CB39: 100n; C_0603_1608Metric_Pad1.08x0.95mm_HandSolder; MPN C0603C104M5RACTU
H2, H3: MountingHole_Pad; MountingHole_3.2mm_M3_Pad_Via
J11: Micro_SD_Card_Det; microSD_HC_Molex_5031821852; MPN 503182-1852
J12: JST-PH; JST_PH_S2B-PH-SM4-TB_1x02-1MP_P2.00mm_Horizontal; MPN 1769
J13: USB_C_Receptacle_USB2.0; USB_C_Recepetacle_JAE_DX07S016JA1; MPN DX07S016JA1R1500
JP8: SD_DET_SEL; SolderJumper-3_P1.3mm_Bridged12_RoundedPad1.0x1.5mm_NumberL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
R65: 100k; R_0603_1608Metric_Pad0.98x0.95mm_HandSolder; MPN RC0603FR-07100KL
R89: 10k; R_0603_1608Metric_Pad0.98x0.95mm_HandSolder; MPN RC0603JR-0710KL
R90, R91: 5.1k; R_0603_1608Metric_Pad0.98x0.95mm_HandSolder; MPN AC0603FR-135K1L
U10: USBLC6-2SC6; SOT-666_Handsoldering; MPN USBLC6-2P6

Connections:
+3V3: C3.1, J11.4 (VDD), JP8.1 (A), R89.2; also elsewhere on the board
+BATT: J12.1; also elsewhere on the board
/A5: J11.10 (DET_A); also elsewhere on the board
/Connectors/USB_CONN_D+: J13.A6 (D+), J13.B6 (D+), U10.4 (I/O2)
/Connectors/USB_CONN_D-: J13.A7 (D-), J13.B7 (D-), U10.6 (I/O1)
/SDIO_CLK: J11.5 (CLK); also elsewhere on the board
/SDIO_CMD: J11.3 (CMD); also elsewhere on the board
/SDIO_D0: J11.7 (DAT0); also elsewhere on the board
/SDIO_D1: J11.8 (DAT1); also elsewhere on the board
/SDIO_D2: J11.1 (DAT2); also elsewhere on the board
/SDIO_D3: J11.2 (DAT3/CD), R89.1; also elsewhere on the board
/USB_DN: U10.1 (I/O1); also elsewhere on the board
/USB_DP: U10.3 (I/O2); also elsewhere on the board
Earth: H2.1, H3.1, J11.11 (SHIELD), J13.S1 (SHIELD); also elsewhere on the board
GND: C3.2, CB39.2, J11.6 (VSS), J12.2, J13.A1 (GND), J13.A12 (GND), J13.B1 (GND), J13.B12 (GND), JP8.3 (B), R90.1, R91.1, U10.2 (GND); also elsewhere on the board
unnamed: J11.9 (DET_B), R65.1
unnamed: J13.A5 (CC1), R91.2
unnamed: J13.B5 (CC2), R90.2
unnamed: JP8.2 (C), R65.2
VBUS: CB39.1, J13.A4 (VBUS), J13.A9 (VBUS), J13.B4 (VBUS), J13.B9 (VBUS), U10.5 (VBUS); also elsewhere on the board

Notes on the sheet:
USB ESD Protection
Connect shield to all external mounting and then to GND at a single point close to the connector. Place all IO connectors (with shields) close to each other.
See application note AN1953
See Application note AN10911
LIPO Battery Connector
SD Card Holder
USB-C Connection

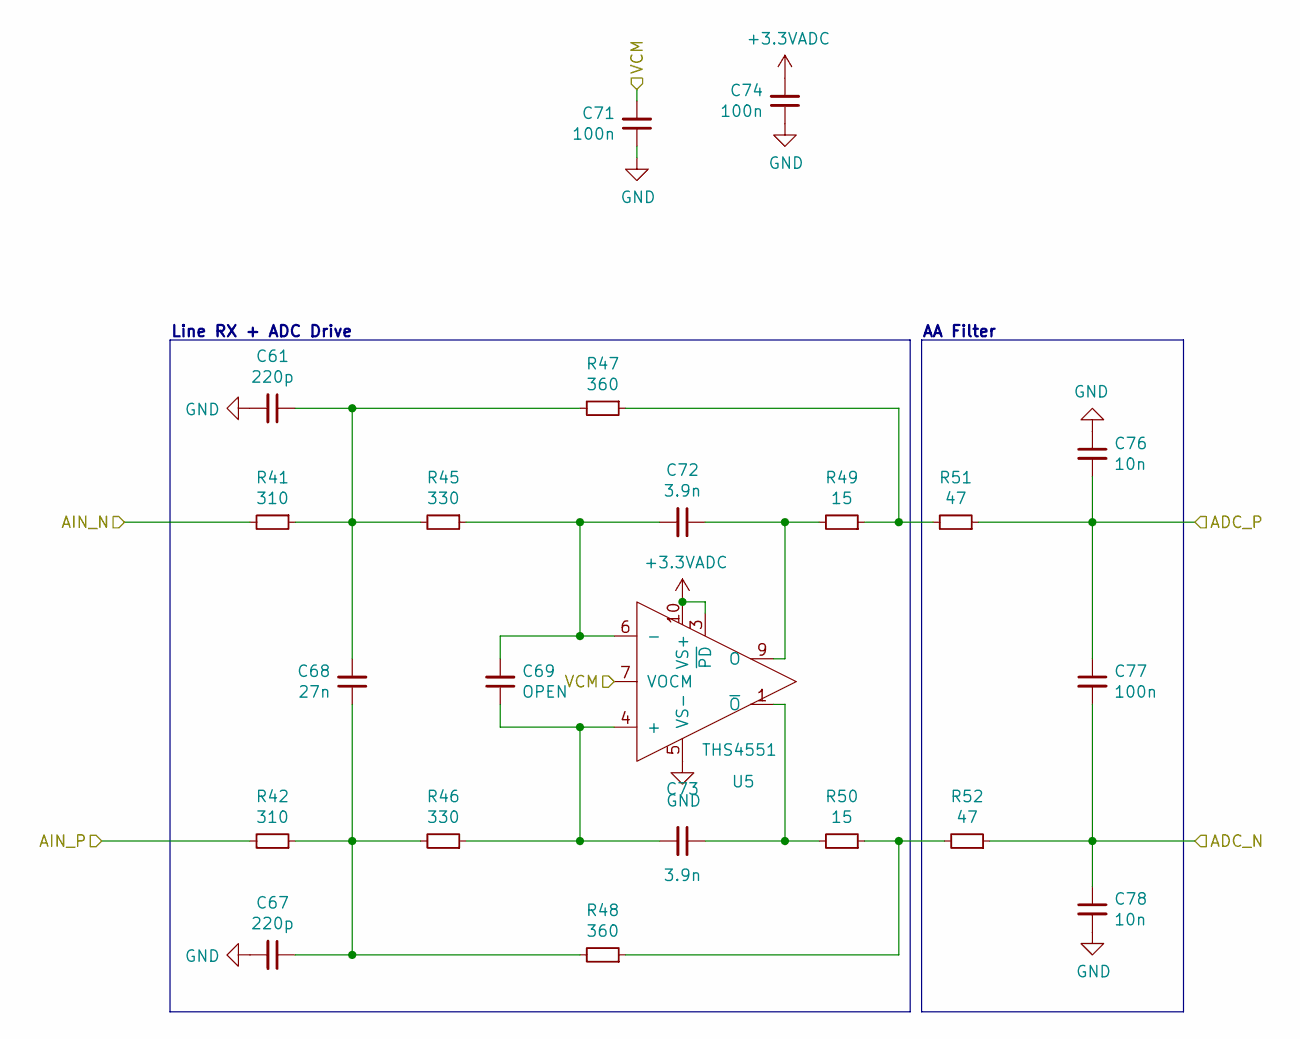
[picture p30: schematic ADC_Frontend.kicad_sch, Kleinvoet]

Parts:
C61, C67: 220p; C_0603_1608Metric_Pad1.08x0.95mm_HandSolder; MPN C0603C221J5GACTU
C68: 27n; C_0603_1608Metric_Pad1.08x0.95mm_HandSolder; MPN CC0603JRX7R9BB273
C69: OPEN; C_0603_1608Metric_Pad1.08x0.95mm_HandSolder
C71, C74, C77: 100n; C_0603_1608Metric_Pad1.08x0.95mm_HandSolder; MPN C0603C104M5RACTU
C72, C73: 3.9n; C_0603_1608Metric_Pad1.08x0.95mm_HandSolder; MPN CC0603JRX7R9BB392
C76, C78: 10n; C_0603_1608Metric_Pad1.08x0.95mm_HandSolder; MPN C0603C103J5RACTU
R41, R42: 310; R_0603_1608Metric_Pad0.98x0.95mm_HandSolder; MPN ERJ-3EKF3090V
R45, R46: 330; R_0603_1608Metric_Pad0.98x0.95mm_HandSolder; MPN ERJ-3EKF3300V
R47, R48: 360; R_0603_1608Metric_Pad0.98x0.95mm_HandSolder; MPN ERJ-3EKF3600V
R49, R50: 15; R_0603_1608Metric_Pad0.98x0.95mm_HandSolder; MPN ERJ-3EKF15R0V
R51, R52: 47; R_0603_1608Metric_Pad0.98x0.95mm_HandSolder; MPN ERJ-3EKF47R0V
U5: THS4551; WQFN-10_RUN; MPN THS4551IRUNR

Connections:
+3.3VADC: C74.2, U5.3 (~PD), U5.10 (VS+); also elsewhere on the board
/ADC_Interface/ADC_2_N: C77.2, C78.1, R52.1; also elsewhere on the board
/ADC_Interface/ADC_2_P: C76.2, C77.1, R51.1; also elsewhere on the board
/ADC_Interface/ADC_PORT_2_SIG_N: R41.2; also elsewhere on the board
/ADC_Interface/ADC_PORT_2_SIG_P: R42.2; also elsewhere on the board
/ADC_Interface/VCM: C71.2, U5.7 (VOCM); also elsewhere on the board
GND: C61.2, C67.2, C71.1, C74.1, C76.1, C78.2, U5.5 (VS-); also elsewhere on the board
unnamed: C61.1, C68.2, R41.1, R45.2, R47.2
unnamed: C67.1, C68.1, R42.1, R46.2, R48.2
unnamed: C69.1, C73.2, R46.1, U5.4 (+)
unnamed: C69.2, C72.2, R45.1, U5.6 (-)
unnamed: C72.1, R49.2, U5.9 (O)
unnamed: C73.1, R50.2, U5.1 (~O)
unnamed: R47.1, R49.1, R51.2
unnamed: R48.1, R50.1, R52.2

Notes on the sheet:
AA Filter
Line RX + ADC Drive

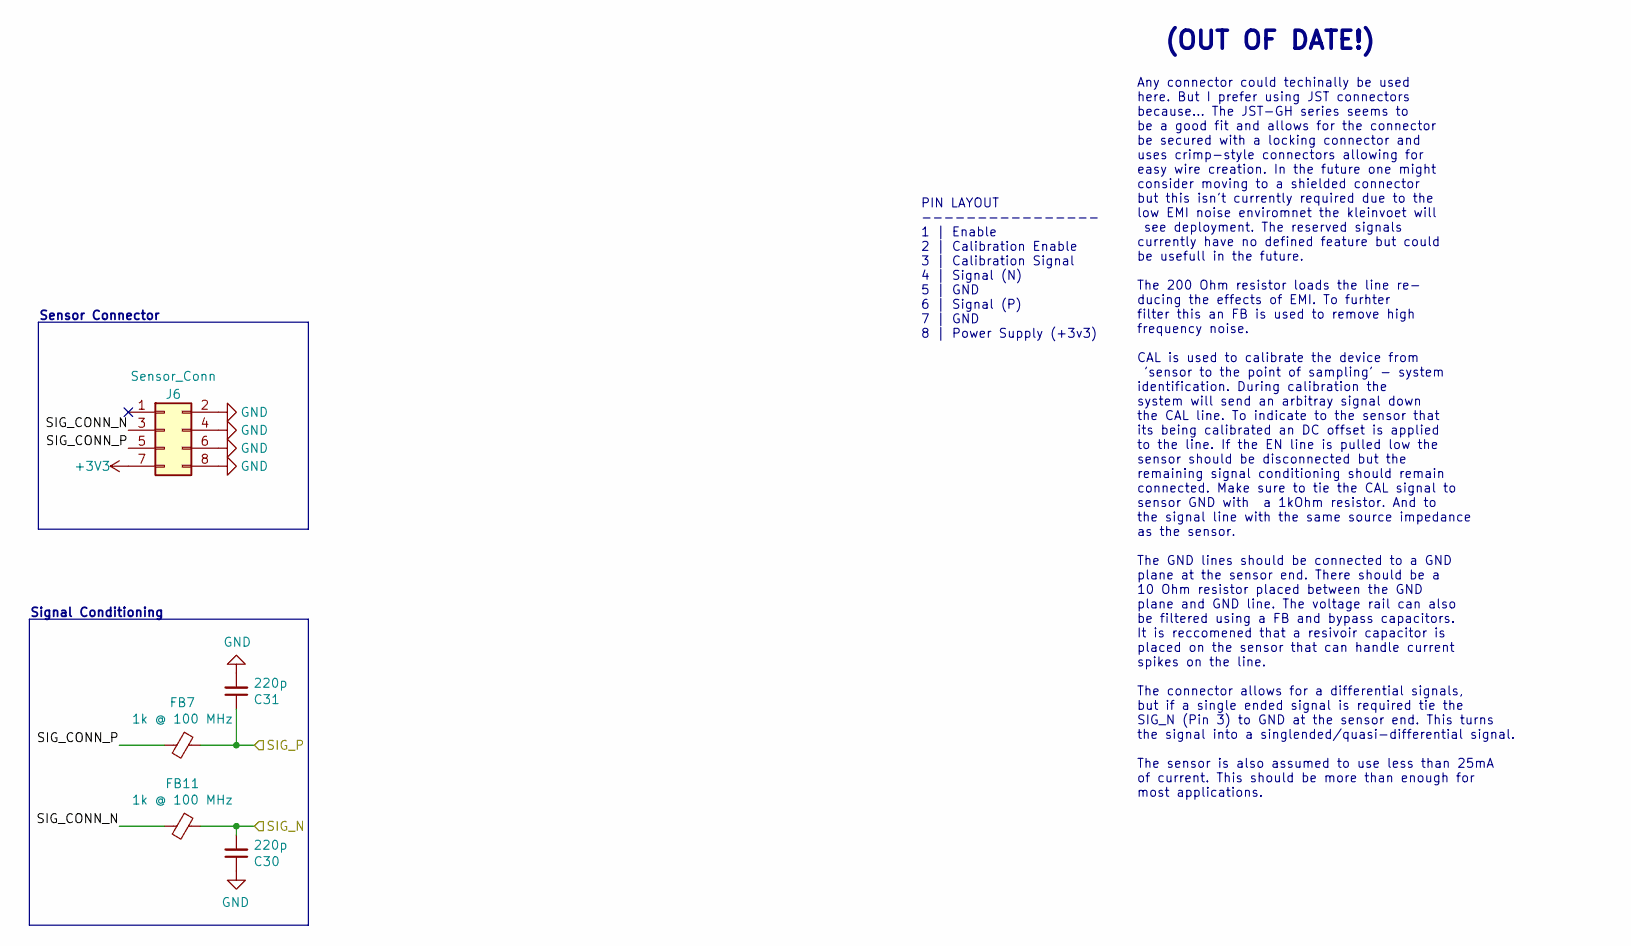
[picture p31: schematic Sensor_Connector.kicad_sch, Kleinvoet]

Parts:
C30, C31: 220p; C_0603_1608Metric_Pad1.08x0.95mm_HandSolder; MPN C0603C221J5GACTU
FB7, FB11: 1k @ 100 MHz; L_0603_1608Metric_Pad1.05x0.95mm_HandSolder; MPN BLM18KG102SN1D
J6: Sensor_Conn; TE_7-215079-8; MPN 7-215079-8, 7-215083-8

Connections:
+3V3: J6.7; also elsewhere on the board
/ADC_Interface/ADC_PORT_2_SIG_N: C30.2, FB11.1; also elsewhere on the board
/ADC_Interface/ADC_PORT_2_SIG_P: C31.1, FB7.1; also elsewhere on the board
/ADC_Interface/Sensor_Conn_2/SIG_CONN_N: FB11.2, J6.3
/ADC_Interface/Sensor_Conn_2/SIG_CONN_P: FB7.2, J6.5
GND: C30.1, C31.2, J6.2, J6.4, J6.6, J6.8; also elsewhere on the board

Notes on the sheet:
Any connector could techinally be used here. But I prefer using JST connectors because... The JST-GH series seems to be a good fit and allows for the connector be secured with a locking connector and uses crimp-style connectors allowing for easy wire creation. In the future one might consider movin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
PIN LAYOUT ---------------- 1 | Enable 2 | Calibration Enable 3 | Calibration Signal 4 | Signal (N) 5 | GND 6 | Signal (P) 7 | GND 8 | Power Supply (+3v3)
Sensor Connector
(OUT OF DATE!)
Signal Conditioning

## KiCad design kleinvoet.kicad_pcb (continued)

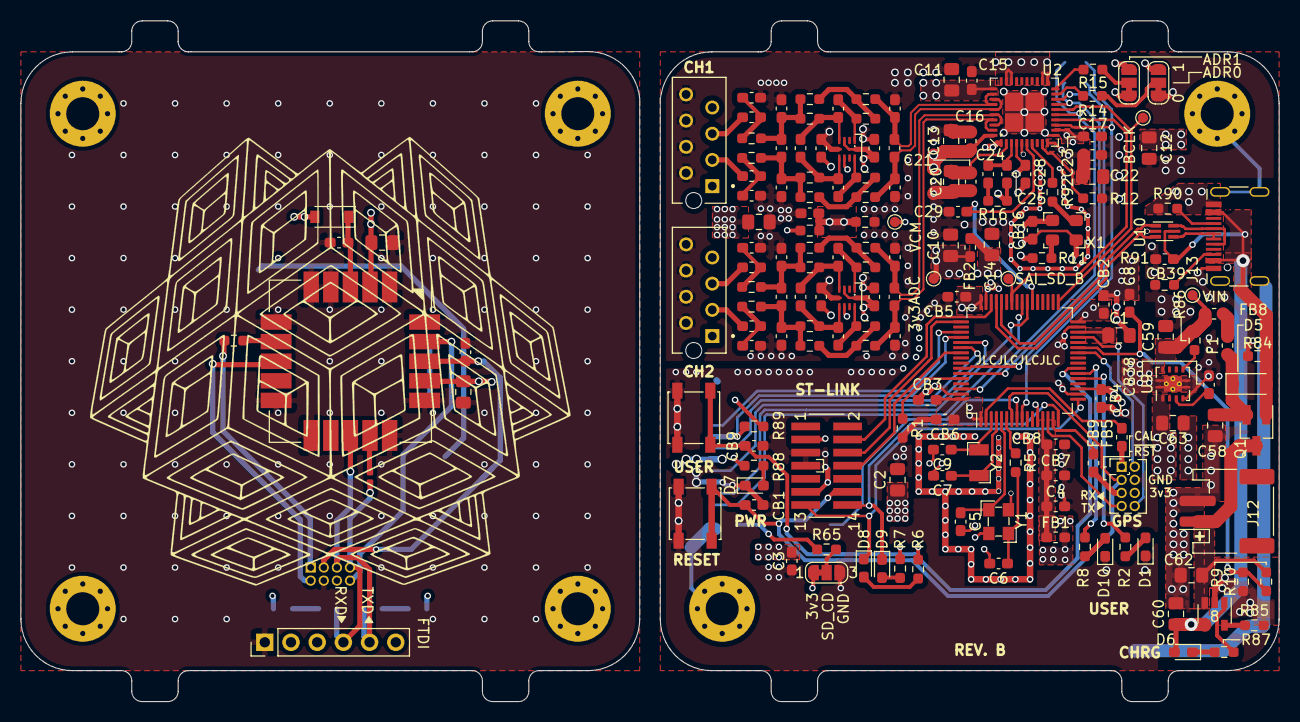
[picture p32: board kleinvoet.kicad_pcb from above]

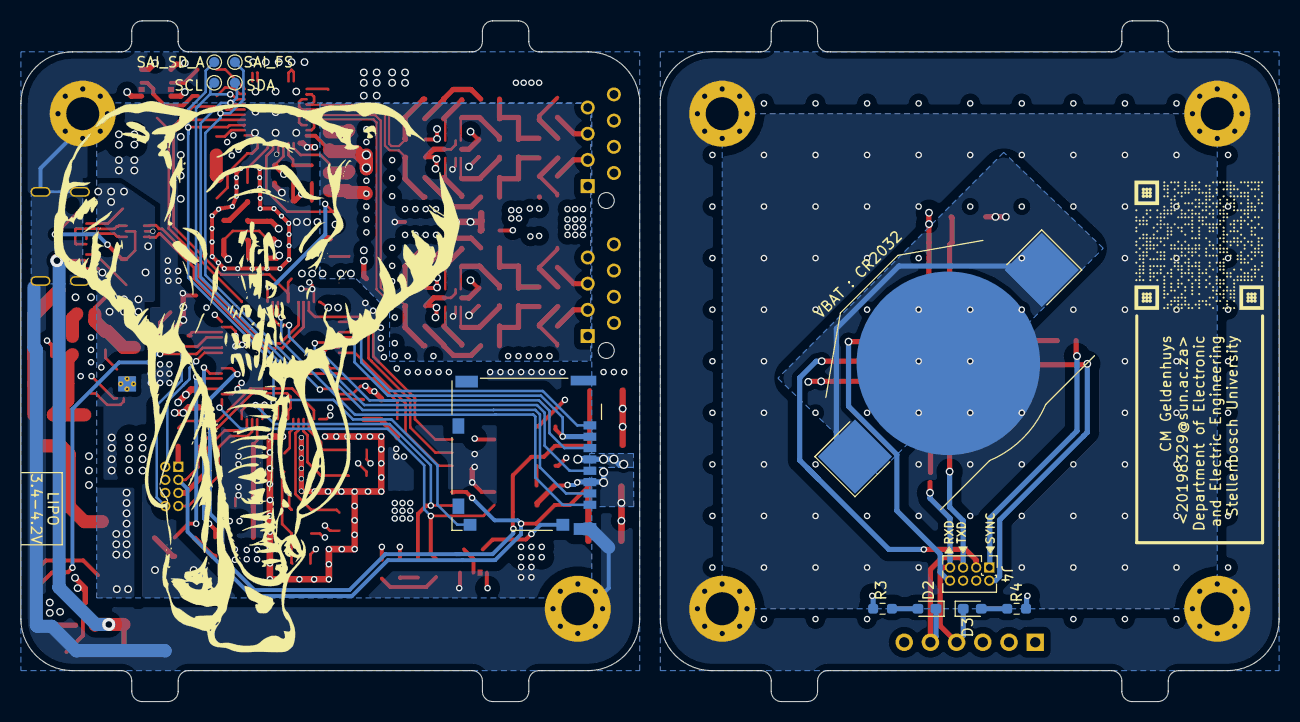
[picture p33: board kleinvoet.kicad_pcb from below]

Board: 4 copper layers, 122.0 x 66.0 mm, 185 parts (11 on the bottom side), 113 nets.

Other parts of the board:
C18, C19, C26, C27: 220p; C_0603_1608Metric_Pad1.08x0.95mm_HandSolder
C34: 27n; C_0603_1608Metric_Pad1.08x0.95mm_HandSolder
C35: OPEN; C_0603_1608Metric_Pad1.08x0.95mm_HandSolder
C37, C40, C43: 100n; C_0603_1608Metric_Pad1.08x0.95mm_HandSolder
C38, C39: 3.9n; C_0603_1608Metric_Pad1.08x0.95mm_HandSolder
C42, C44: 10n; C_0603_1608Metric_Pad1.08x0.95mm_HandSolder
FB3, FB4: Ferrite_Bead_Small; L_0603_1608Metric_Pad1.05x0.95mm_HandSolder
J3: Sensor_Conn; TE_7-215079-8
R17, R18: 310; R_0603_1608Metric_Pad0.98x0.95mm_HandSolder
R21, R22: 330; R_0603_1608Metric_Pad0.98x0.95mm_HandSolder
R23, R24: 360; R_0603_1608Metric_Pad0.98x0.95mm_HandSolder
R25, R26: 15; R_0603_1608Metric_Pad0.98x0.95mm_HandSolder
R27, R28: 47; R_0603_1608Metric_Pad0.98x0.95mm_HandSolder
U3: THS4551; WQFN-10_RUN

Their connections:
+3.3VADC: C40.2, U3.3, U3.10; also elsewhere on the board
+3V3: J3.7; also elsewhere on the board
/ADC_Interface/ADC_1_N: C43.2, C44.1, R28.1; also elsewhere on the board
/ADC_Interface/ADC_1_P: C42.2, C43.1, R27.1; also elsewhere on the board
/ADC_Interface/ADC_PORT_1_SIG_N: C18.2, FB4.1, R17.2
/ADC_Interface/ADC_PORT_1_SIG_P: C19.1, FB3.1, R18.2
/ADC_Interface/Sensor_Conn_1/SIG_CONN_N: FB4.2, J3.3
/ADC_Interface/Sensor_Conn_1/SIG_CONN_P: FB3.2, J3.5
/ADC_Interface/VCM: C37.2, U3.7; also elsewhere on the board
GND: C18.1, C19.2, C26.2, C27.2, C37.1, C40.1, C42.1, C44.2, J3.2, J3.4, J3.6, J3.8, U3.5; also elsewhere on the board
unnamed: C26.1, C34.2, R17.1, R21.2, R23.2
unnamed: C27.1, C34.1, R18.1, R22.2, R24.2
unnamed: C35.1, C39.2, R22.1, U3.4
unnamed: C35.2, C38.2, R21.1, U3.6
unnamed: C38.1, R25.2, U3.9
unnamed: C39.1, R26.2, U3.1
unnamed: R23.1, R25.1, R27.2
unnamed: R24.1, R26.1, R28.2

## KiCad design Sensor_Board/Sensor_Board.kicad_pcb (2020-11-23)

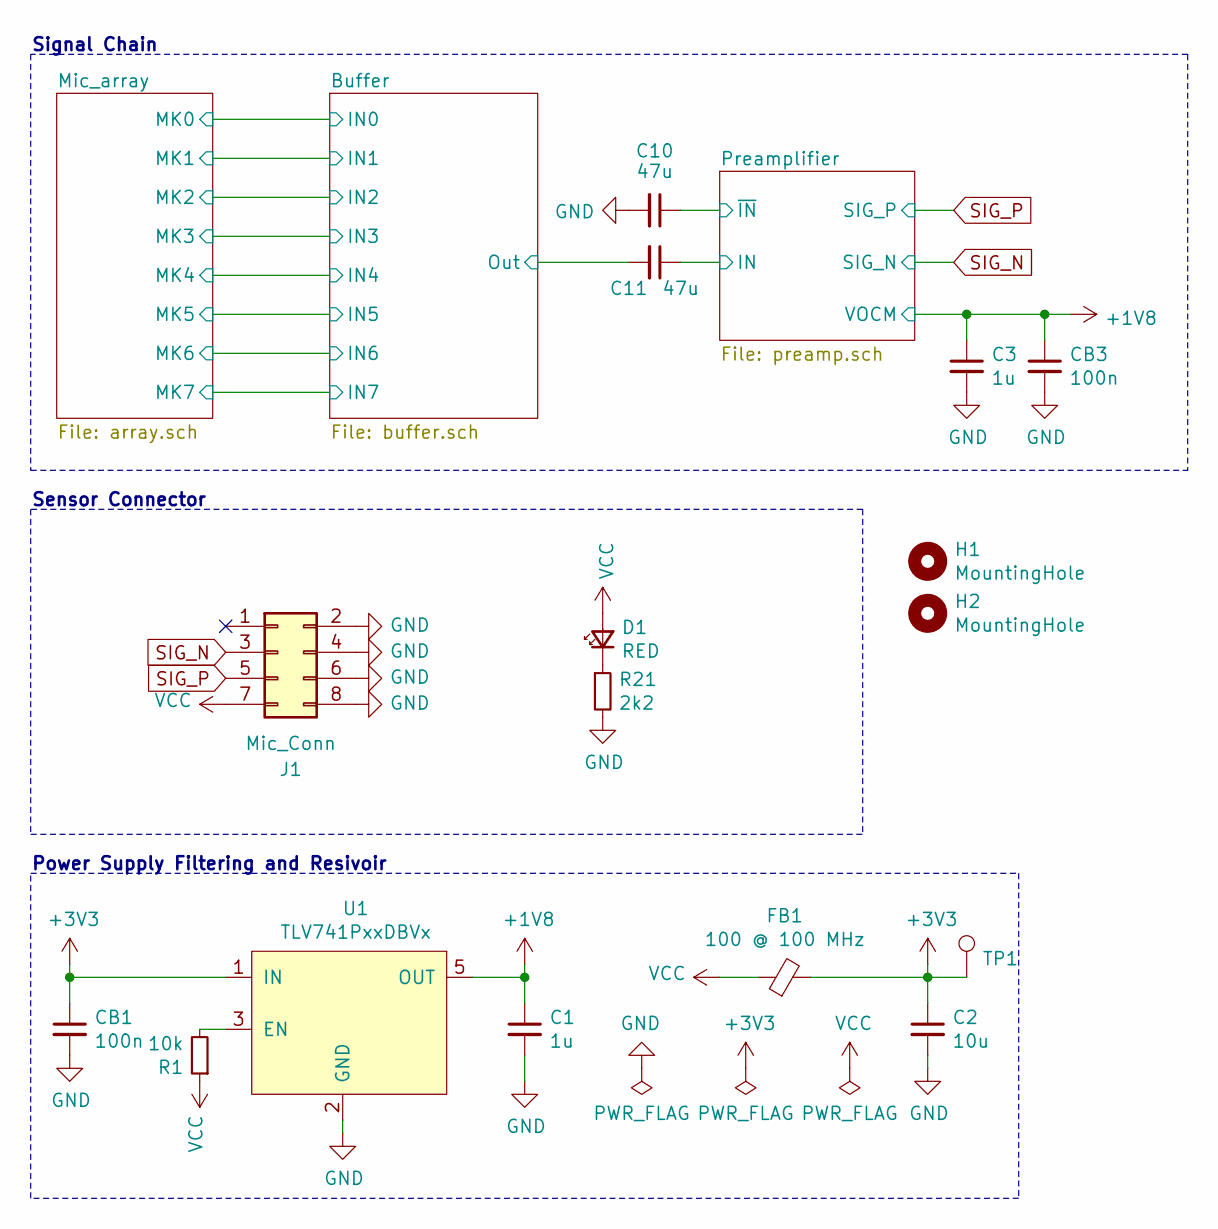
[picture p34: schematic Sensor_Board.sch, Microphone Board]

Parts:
C1, C3: 1u; C_0603_1608Metric_Pad1.08x0.95mm_HandSolder; MPN C0603C105K8RACTU
C2: 10u; C_0805_2012Metric_Pad1.18x1.45mm_HandSolder; MPN C0805C106K9PACTU
C10, C11: 47u; C_1206_3216Metric_Pad1.33x1.80mm_HandSolder; MPN GRM31CR60J107KE39K
CB1, CB3: 100n; C_0603_1608Metric_Pad1.08x0.95mm_HandSolder; MPN C0603C104M5RACTU
D1: RED; LED_0603_1608Metric_Pad1.05x0.95mm_HandSolder; MPN SML-D12U8WT86C
FB1: 100 @ 100 MHz; L_0603_1608Metric_Pad1.05x0.95mm_HandSolder; MPN BLM18EG101TZ1D
H1, H2: MountingHole; MountingHole_3.2mm_M3_Pad_Via
J1: Mic_Conn; TE_7-215079-8; MPN 7-215079-8, 7-215083-8
R1: 10k; R_0603_1608Metric_Pad0.98x0.95mm_HandSolder; MPN RC0603JR-0710KL
R21: 2k2; R_0603_1608Metric_Pad0.98x0.95mm_HandSolder; MPN ERJ-3EKF2201V
TP1: TestPoint; TestPoint_Pad_D1.0mm; MPN ICS-40300
U1: TLV741PxxDBVx; SOT-23-5; MPN TLV74118PDBVR

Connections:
+1V8: C1.1, C3.1, CB3.1, U1.5 (OUT); also elsewhere on the board
+3V3: C2.1, CB1.1, FB1.2, TP1.1, U1.1 (IN); also elsewhere on the board
/Buffer/Out: C11.2; also elsewhere on the board
/Preamplifier/IN: C11.1; also elsewhere on the board
/Preamplifier/~IN: C10.1; also elsewhere on the board
GND: C1.2, C2.2, C3.2, C10.2, CB1.2, CB3.2, J1.2, J1.4, J1.6, J1.8, R21.2, U1.2 (GND); also elsewhere on the board
unnamed: D1.1 (K), R21.1
unnamed: R1.2, U1.3 (EN)
SIG_N: J1.3; also elsewhere on the board
SIG_P: J1.5; also elsewhere on the board
VCC: D1.2 (A), FB1.1, J1.7, R1.1

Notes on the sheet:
Power Supply Filtering and Resivoir
Sensor Connector
Signal Chain

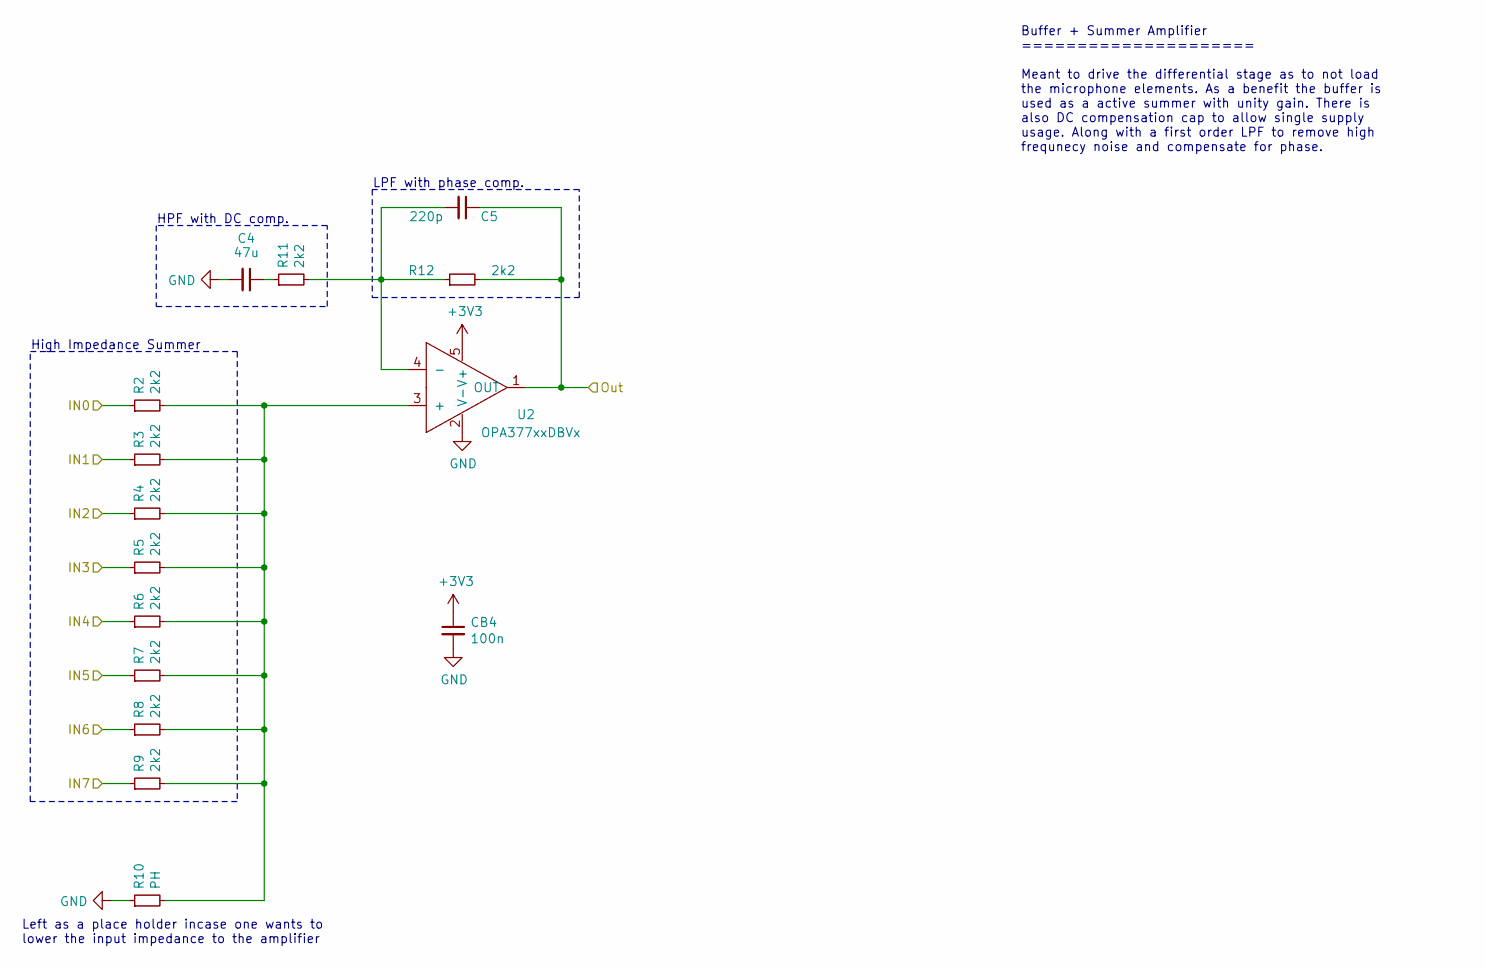
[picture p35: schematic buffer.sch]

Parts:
C4: 47u; C_1206_3216Metric_Pad1.33x1.80mm_HandSolder; MPN GRM31CR60J107KE39K
C5: 220p; C_0603_1608Metric_Pad1.08x0.95mm_HandSolder; MPN C0603C221J5GACTU
CB4: 100n; C_0603_1608Metric_Pad1.08x0.95mm_HandSolder; MPN C0603C104M5RACTU
R2, R3, R4, R5, R6, R7, R8, R9, R11, R12: 2k2; R_0603_1608Metric_Pad0.98x0.95mm_HandSolder; MPN ERJ-3EKF2201V
R10: PH; R_0603_1608Metric_Pad0.98x0.95mm_HandSolder
U2: OPA377xxDBVx; SOT-23-5; MPN OPA377AIDBVR

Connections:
+3V3: CB4.1, U2.5 (V+); also elsewhere on the board
/Buffer/IN0: R2.1; also elsewhere on the board
/Buffer/IN1: R3.1; also elsewhere on the board
/Buffer/IN2: R4.1; also elsewhere on the board
/Buffer/IN3: R5.1; also elsewhere on the board
/Buffer/IN4: R6.1; also elsewhere on the board
/Buffer/IN5: R7.1; also elsewhere on the board
/Buffer/IN6: R8.1; also elsewhere on the board
/Buffer/IN7: R9.1; also elsewhere on the board
/Buffer/Out: C5.1, R12.2, U2.1 (OUT); also elsewhere on the board
GND: C4.2, CB4.2, R10.1, U2.2 (V-); also elsewhere on the board
unnamed: C4.1, R11.1
unnamed: C5.2, R11.2, R12.1, U2.4 (-)
unnamed: R2.2, R3.2, R4.2, R5.2, R6.2, R7.2, R8.2, R9.2, R10.2, U2.3 (+)

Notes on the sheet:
Buffer + Summer Amplifier ===================== Meant to drive the differential stage as to not load the microphone elements. As a benefit the buffer is used as a active summer with unity gain. There is also DC compensation cap to allow single supply usage. Along with a first order LPF to remove hi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
LPF with phase comp.
HPF with DC comp.
High Impedance Summer
Left as a place holder incase one wants to lower the input impedance to the amplifier

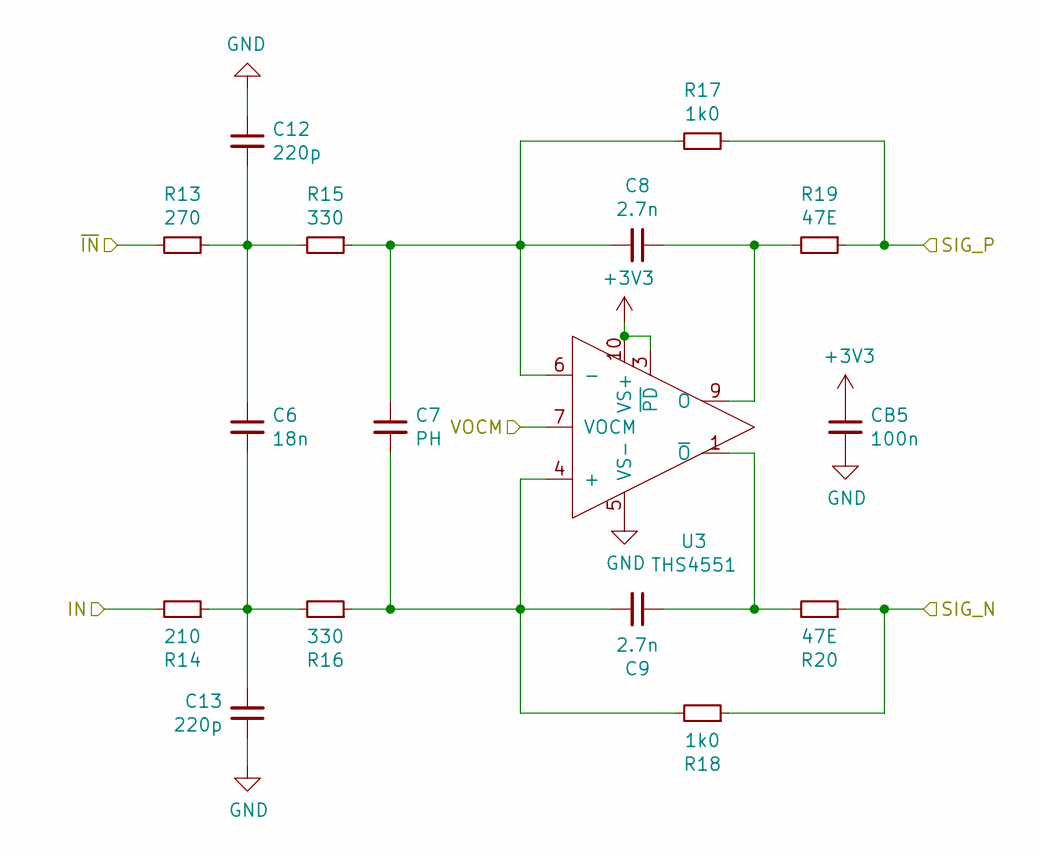
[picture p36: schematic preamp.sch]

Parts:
C6: 18n; C_0603_1608Metric_Pad1.08x0.95mm_HandSolder; MPN CC0603JRX7R8BB183
C7: PH; R_0603_1608Metric_Pad0.98x0.95mm_HandSolder
C8, C9: 2.7n; C_0603_1608Metric_Pad1.08x0.95mm_HandSolder; MPN CC0603JRX7R9BB272
C12, C13: 220p; C_0603_1608Metric_Pad1.08x0.95mm_HandSolder; MPN C0603C221J5GACTU
CB5: 100n; C_0603_1608Metric_Pad1.08x0.95mm_HandSolder; MPN C0603C104M5RACTU
R13: 270; R_0603_1608Metric_Pad0.98x0.95mm_HandSolder; MPN ERJ-3EKF2700V
R14: 210; R_0603_1608Metric_Pad0.98x0.95mm_HandSolder; MPN ERJ-3EKF2100V
R15, R16: 330; R_0603_1608Metric_Pad0.98x0.95mm_HandSolder; MPN ERJ-3EKF3300V
R17, R18: 1k0; R_0603_1608Metric_Pad0.98x0.95mm_HandSolder; MPN ERJ-3EKF1001V
R19, R20: 47E; R_0603_1608Metric_Pad0.98x0.95mm_HandSolder; MPN ERJ-3EKF47R0V
U3: THS4551; WQFN-10_RUN; MPN THS4551IRUNR

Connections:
+1V8: U3.7 (VOCM); also elsewhere on the board
+3V3: CB5.1, U3.3 (~PD), U3.10 (VS+); also elsewhere on the board
/Preamplifier/IN: R14.2; also elsewhere on the board
/Preamplifier/~IN: R13.2; also elsewhere on the board
GND: C12.1, C13.1, CB5.2, U3.5 (VS-); also elsewhere on the board
unnamed: C7.1, C8.2, R15.1, R17.2, U3.6 (-)
unnamed: C7.2, C9.2, R16.1, R18.2, U3.4 (+)
unnamed: C8.1, R19.2, U3.9 (O)
unnamed: C9.1, R20.2, U3.1 (~O)
unnamed: C6.1, C12.2, R13.1, R15.2
unnamed: C6.2, C13.2, R14.1, R16.2
SIG_N: R18.1, R20.1; also elsewhere on the board
SIG_P: R17.1, R19.1; also elsewhere on the board


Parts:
C14, C15: 1u; C_0603_1608Metric_Pad1.08x0.95mm_HandSolder; MPN C0603C105K8RACTU
CB6, CB7, CB8, CB9, CB10, CB11, CB12, CB13: 100n; C_0603_1608Metric_Pad1.08x0.95mm_HandSolder; MPN C0603C104M5RACTU
MK1, MK2, MK3, MK4, MK5, MK6, MK7, MK8: MIC_ICS_40300; MEMS_Mic_ICS-40300; MPN ICS-40300

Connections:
+1V8: C14.1, C15.1, CB6.1, CB7.1, CB8.1, CB9.1, CB10.1, CB11.1, CB12.1, CB13.1, MK1.5 (VDD), MK2.5 (VDD), MK3.5 (VDD), MK4.5 (VDD), MK5.5 (VDD), MK6.5 (VDD), MK7.5 (VDD), MK8.5 (VDD); also elsewhere on the board
/Buffer/IN0: MK4.1 (OUTPUT); also elsewhere on the board
/Buffer/IN1: MK3.1 (OUTPUT); also elsewhere on the board
/Buffer/IN2: MK2.1 (OUTPUT); also elsewhere on the board
/Buffer/IN3: MK1.1 (OUTPUT); also elsewhere on the board
/Buffer/IN4: MK5.1 (OUTPUT); also elsewhere on the board
/Buffer/IN5: MK6.1 (OUTPUT); also elsewhere on the board
/Buffer/IN6: MK7.1 (OUTPUT); also elsewhere on the board
/Buffer/IN7: MK8.1 (OUTPUT); also elsewhere on the board
GND: C14.2, C15.2, CB6.2, CB7.2, CB8.2, CB9.2, CB10.2, CB11.2, CB12.2, CB13.2, MK1.2 (GND), MK1.3 (GND), MK1.4 (GND), MK1.6 (GND), MK2.2 (GND), MK2.3 (GND), MK2.4 (GND), MK2.6 (GND), MK3.2 (GND), MK3.3 (GND), MK3.4 (GND), MK3.6 (GND), MK4.2 (GND), MK4.3 (GND), MK4.4 (GND), MK4.6 (GND), MK5.2 (GND), MK5.3 (GND), MK5.4 (GND), MK5.6 (GND), MK6.2 (GND), MK6.3 (GND), MK6.4 (GND), MK6.6 (GND), MK7.2 (GND), MK7.3 (GND), MK7.4 (GND), MK7.6 (GND), MK8.2 (GND), MK8.3 (GND), MK8.4 (GND), MK8.6 (GND); also elsewhere on the board



Board: 4 copper layers, 68.0 x 38.0 mm, 65 parts (19 on the bottom side), 28 nets.

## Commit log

2020-06-03 Setup project
    Create basic project structure and add kicad project libraries
    (gitmodule) at _HEAD_ of _master_.
    [kleinvoet.kicad_pcb, kleinvoet.sch]
2020-06-03 Design GPS section
    Implement SAM-M8Q GPS module design based on information from the
    hardware integration guide.
    -- Layout main module
    -- Configure power section
    -- Add external connections
    -- Add EMI to important signals
    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
    [kleinvoet.sch]
2020-06-03 Design ADC Section
    -- Update libs with sch of ADS131M04
    -- Design analogue frontend (AA filter)
    -- Design sensor connector
    -- Layout ADC with power section
    [ADC_Frontend.sch, Sensor_Connector.sch, kleinvoet.sch]
2020-06-05 Change sensor connector to JST-GH
    [ADC_Frontend.sch, Sensor_Connector.sch, kleinvoet.sch]
2020-06-05 Update sensor connection specifications
    [Sensor_Connector.sch]
2020-06-08 Move GNSS module to own sheet
    [ADC_Frontend.sch, GNSS_Module.sch, Sensor_Connector.sch, kleinvoet.sch]
2020-06-08 Move ADC module to own sheet
    [ADC_Frontend.sch, ADC_Interface.sch, GNSS_Module.sch, Sensor_Connector.sch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]
2020-06-08 Design Power(LDO) section
    [ADC_Frontend.sch, ADC_Interface.sch, GNSS_Module.sch, Power.sch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]
2020-06-08 Design Power (Dual Rail) section
    Also add USB-C connection
    [ADC_Interface.sch, GNSS_Module.sch, Power.sch, kleinvoet.sch]
2020-06-08 Design LIPO charge circuit
    [Power.sch]
2020-06-08 Design SD card interface
    [ADC_Frontend.sch, ADC_Interface.sch, Connectors.sch, GNSS_Module.sch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]
2020-06-08 Update Analogue Connector's Power
    [Sensor_Connector.sch]
2020-06-11 Design Mic. Board
    [ADC_Frontend.sch, ADC_Interface.sch, Connectors.sch, GNSS_Module.sch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]
2020-06-11 Change Connector Layout
    Also add Mic. board to connectors
    [ADC_Interface.sch, Microphone_Sensor.sch, Power.sch, Sensor_Connector.sch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]
2020-06-11 Fix up some cap
    [ADC_Frontend.sch, ADC_Interface.sch, Connectors.sch, GNSS_Module.sch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]
2020-06-13 Design MCU section
    [ADC_Frontend.sch, ADC_Interface.sch, Connectors.sch, GNSS_Module.sch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]
2020-06-15 Remove SD pullup resistors
    [Connectors.sch]
2020-06-15 Finalise design
    [ADC_Interface.sch, Connectors.sch, GNSS_Module.sch, kleinvoet.sch]
2020-06-15 Add PWR Flags
    [ADC_Frontend.sch, ADC_Interface.sch, Connectors.sch, GNSS_Module.sch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]
2020-06-17 Simulate Battery Switching Cicruit
2020-06-17 Assign footprints for all components
    [ADC_Frontend.sch, ADC_Interface.sch, Connectors.sch, GNSS_Module.sch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]
2020-06-17 Change voltage polarity diode
    [GNSS_Module.sch, Microphone_Sensor.sch, Power.sch, Sensor_Connector.sch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]
2020-06-17 Change Mic Preamp
    [ADC_Frontend.sch, ADC_Interface.sch, Connectors.sch, GNSS_Module.sch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]
2020-06-18 Fix BOM ref
    [ADC_Frontend.sch, ADC_Interface.sch, Connectors.sch, GNSS_Module.sch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]
2020-06-18 Change Sensor Connectors
    [ADC_Frontend.sch, ADC_Interface.sch, Connectors.sch, GNSS_Module.sch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]
2020-06-18 Setup PCB
    [Microphone_Sensor.sch, Sensor_Connector.sch, kleinvoet.kicad_pcb]
2020-06-24 PCB Layout Checkpoint
    [ADC_Frontend.sch, ADC_Interface.sch, Connectors.sch, GNSS_Module.sch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]
2020-07-02 Major Commit with Final PCB Design
    [ADC_Frontend.sch, ADC_Interface.sch, Connectors.sch, GNSS_Module.sch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]
2020-07-02 Move JLC Order number
    [kleinvoet.kicad_pcb]
2020-07-05 CHange to single 3 designs to save cost
    [ADC_Interface.sch, Connectors.sch, GNSS_Module.sch, Microphone_Sensor.sch]
2020-07-06 Board Rev. A
    PCB sent for production at JLC PCB. 5 boards with 3 different designs
    placed in a panel.
    [TRXElectronics_Quotation.xlsx, kleinvoet-B_Cu.gbl, kleinvoet-B_Mask.gbs, kleinvoet-B_SilkS.gbo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]
2020-08-14 Parts received
    [BOM_inventory.ods]
2020-08-17 Soldering Workorder
    [BOM_inventory.ods]
2020-08-27 Note mistakes on board
2020-08-28 Add more board improvements
2020-09-16 Fix Mic0 PCB mistakes
    [Microphone_Sensor.sch]
2020-09-30 Fix Microphone sensor Board
    NOTE: Layout still needs to be replicated
    [Microphone_Sensor.sch]
2020-10-07 Try split up project to multiboard
    NOTE: There was a warning about libs being out of date and the USB-C
    connector. This was partly due to the 'libs' dir not being up to date
    but the USB-C looks like a global update.
    [Connectors.sch, GNSS_Module.sch, Microphone_Sensor.sch]
2020-10-13 Design synth for preamp with 5th order filtering
    ===============================================
    Squashed commit of the following:
    ===============================================
    commit f1db44bd3b0851ef675320c3edaa554ff146952f
    Author: CM Geldenhuys <20198329@sun.ac.za>
    Date: Tue Oct 13 13:36:53 2020 +0200
    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
    [MFB_Design_User.xls]
2020-10-21 Merge 'feature/mic-board'
    Split out Sensor_board to own project for easier panelising later.
    Allows also for better independent development.
    commit 5c89ddf7514428c762fb7c211bc44fe947092eb1
    Date: Wed Oct 21 14:34:31 2020 +0200
    Add emblem
    commit bbe0a53b49b0ec3aa4e2f65424c556ce99509fe4
    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
    [ADC_Frontend.sch, ADC_Interface.sch, Connectors.sch, GNSS_Module.sch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]
2020-10-21 Update ICS40300 MPN
    [array.sch]
2020-11-02 New ADC board layout
    Merge feature/kv-new-adc
    commit d560af3129baffdc71a13a7fa7beda6d7e4b1bbe
    Date: Mon Nov 2 10:16:05 2020 +0200
    Change board layout
    commit e0e102b1b715915958904bd07514080422fcc802
    Date: Mon Nov 2 08:42:49 2020 +0200
    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
    [ADC_Frontend.sch, ADC_Interface.sch, Connectors.sch, GNSS_Module.sch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]
2020-11-02 Fix Board dim.
    [kleinvoet.kicad_pcb]
2020-11-02 Fix KICAD! & DRC
    [kleinvoet.kicad_pcb]
2020-11-02 Start panel
    [panel.kicad_pcb]
2020-11-02 Ready for panelisation
    [GNSS_Module.sch, Power.sch, kleinvoet.kicad_pcb]
2020-11-02 Misc. changes
    [kleinvoet.kicad_pcb]
2020-11-03 Update pinout
    [ADC_Frontend.sch, Sensor_Connector.sch, kleinvoet.kicad_pcb, kleinvoet.sch]
2020-11-03 Update connector
    [Sensor_Board.kicad_pcb, Sensor_Board.sch, Sensor_Connector.sch, preamp.sch]
2020-11-03 Route update conn.
    [Sensor_Board.kicad_pcb, Sensor_Board.sch]
2020-11-03 Misc changes
    [Sensor_Board.kicad_pcb]
2020-11-03 Reference panel
    [Sensor_Board.kicad_pcb, kleinvoet.kicad_pcb, panel.kicad_pcb]
2020-11-03 Complete panel
    [Sensor_Board.kicad_pcb]
2020-11-03 Export gerbers
    [kleinvoet-B_Cu.gbl, kleinvoet-B_Mask.gbs, kleinvoet-B_SilkS.gbo, kleinvoet-Cmts_User.gbr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]
2020-11-04 Fix USB diff. GND layer
    [kleinvoet.kicad_pcb]
2020-11-04 Add layer info
    [panel.kicad_pcb]
2020-11-04 Fix misc. issue
    [kleinvoet.kicad_pcb, kleinvoet.sch]
2020-11-09 Add 10k MPN
    [Sensor_Board.sch]
2020-11-13 Fix drill size for man.
    [Sensor_Board.kicad_pcb, kleinvoet.kicad_pcb]
2020-11-23 Add Fab layer (mic)
    [Sensor_Board.kicad_pcb]
2020-11-23 Add Fab layer (MB)
    [kleinvoet.kicad_pcb]
2020-11-23 Gen FAB
    [kleinvoet.kicad_pcb]
2021-03-03 Start modeling case
    [kleinvoet_gps.step]
2021-03-04 Finish case
    [Battery_holder.stl, GPS_holder.stl, Main_holder.stl]
2021-03-09 Update case design
    [Battery_holder.stl, GPS_holder.stl, Main_holder.stl]
2021-03-09 Create mic holes
2021-03-10 Finish drill workorder
2021-03-10 Add sensor board mount holes
2021-03-12 Add spacer
    [GPS_holder.stl, Main_holder.stl, Sensorboard_spacer.stl]
2021-03-16 Fix tol. on spacer
    [Sensorboard_spacer.stl]
2021-03-16 Case revisions
    [GPS_holder.stl, Main_holder.stl, Sensorboard_spacer.stl]
2021-03-26 Final changes to case
    [GPS_holder.stl, Main_holder.stl, Sensorboard_spacer.stl]
2021-04-06 Move tools to separate folder
    Update filter design script
    [MFB_Design_User.xls]
2021-04-06 Add filter design PDF from TI
2021-04-06 Better document filter design
2021-04-06 Add export functionality to filter design
2021-04-08 Add PCB screw holes
    [GPS_holder.stl, Main_holder.stl, Sensorboard_spacer.stl]
2021-05-18 Enlarge SD card clearance
    [Main_holder.stl]
2021-05-18 Fix screw holes
    [Main_holder.stl]
2021-05-19 New mic cutout
    [GPS_holder.stl]
2022-05-10 (cad) create single microphone cut out
2022-05-10 (pcb) export board images
    [ADC_Frontend.kicad_sch, ADC_Interface.kicad_sch, Connectors.kicad_sch, GNSS_Module.kicad_sch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]
2022-05-11 add exploded disassembly view
    commit 33c77791b966c18d4545fea2d25353900eec7e89
    Author: CM Geldenhuys <4649249+CMGeldenhuys@users.noreply.github.com>
    Date: Wed May 11 14:50:28 2022 +0200
    change board colors
    commit f795a82866af1a41bf84c1e0fe859adeabf3a879
    Author: CM Geldenhuys <4649249+CMGeldenhuys@users.noreply.github.com>
    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
2023-03-27 (repo) add sample recording
2023-03-27 (repo) clean up
    [BOM_inventory.ods, TRXElectronics_Quotation.xlsx, bom_order.ods]
2023-04-11 (docs) add pcb panel PDF files
2023-04-11 (docs) add pcb PDF files
2023-04-11 (docs) update README with PCB layout and sch PDFs

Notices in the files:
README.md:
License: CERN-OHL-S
